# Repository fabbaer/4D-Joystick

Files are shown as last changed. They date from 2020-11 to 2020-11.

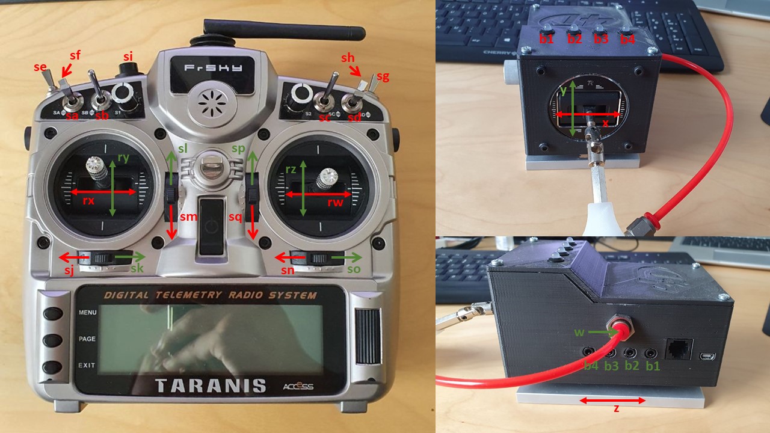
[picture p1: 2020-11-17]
documentation/mapping.jpg

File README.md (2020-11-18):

# 4D-Joystick

## Introduction
The 4D-Joystick allows people with physical disabilities to control complex RC-toys, like plains or multicopper. The RC-toys are controlled via a mouthpiece, a pressure sensor and movements of the head.

The system is divided into two units. The joystickunit is the user interface. It records the user inputs, processes them and forwards them to the remoteunit. The remoteunit is responsible for the communication with the RC-toy.

### Joystickunit
The joystickunit is the main part of the system and handles all user interactions. The heart of the system is a self-developed hardware with a Cortex-M4-Controller. The firmware offers a command-line-interface (CLI) via a USB connection to configure the system. Up to 32 different configurations can be stored on the joystickunit, each offering a flexible mapping of all inputs and outputs and configurations like deadzones. 

The joystickunit can either be powered via USB or via the remoteunit. All peripherals are placed inside a 3D-printed enclosure, which can be mounted on a stand. On the outside of the housing a display and a rotary button is placed, which can be used to load different configurations and display system information. Additionally, there are four headphone jacks to connect external buttons, which can be used to control the digital channels of the remote control. The buttons can be chosen to fit the user's needs and can for example be pressed with a foot or finger. 

The analogue channels are controlled via a mouthpiece. Three of the four degrees of freedom are controlled via movements of the head in up, down, left, right, forward and backward direction. The fourth degree of freedom is controlled via a pressure sensor, which is connected to the mouthpiece. 

The firmware of the joystickunit is designed to be future-proof. In future applications, the joystickunit can for example be used as an input device for a computer or a game console. However, none of these applications are currently implemented, but many parts of the firmware are designed that this can be easily done in future. 

### Remoteunit
The remoteunit handles the communication with the RC-toy. A conventional RC-toy-remote (FrSky Taranis X9D Plus v2019) with OpenTX as main firmware is used as a basis for this unit.

The joystickunit needs to gain control over the input-devices of the remote-control (joysticks and buttons). Therefore, an additional PCB is added to the remote, which is placed right between the input devices and the main controller board. It is able to read the input-devices and control the corresponding inputs of the main controller board. Additionally, it is able to communicate with the joystickunit via SPI.

If the joystick unit is connected to this hardware, the board samples the input devices and sends this data to the joystick unit, where it can be used as input data. Parallel to this, the joystick unit sends the data for the output channels, which are then set by the board accordingly. Therefore, the joystick unit gains full access over the inputs of the remote unit.

If the joystick unit is not connected to the remoteunit, the additional board acts transparent and copies the inputs directly to the outputs. Therefore, the remote control can be normally used without the joystick unit.

## Content
### Folder "firmware"
Contains the firmware of the joystickunit and the remoteunit. Both firmwares were originally developed in STM32CubeIDE. The corresponding project files for this IDE were also included in this directory. 

To flash the firmware to the units a JTAG-programmer (e.g. ST-Link) and an adapter (e.g. Olimex ARM-JTAG-20-10) is needed.
 
### Folder "hardware"
Contains the hardware for both units. The PCBs were developed in Autodesk EAGLE. However, the folder contains also a PDF of the schematics and GERBER-data for manufacturing.

**NOTE:** The bill of material can be found in the documentation-folder.

### Folder "mechanics"

Contains the 3D-models of the enclosure for the joystickunit, which can be printed with a 3D-printer. They were developed in Autodesk Fusion 360.

### Folder "documentation"
Contains a bill of material and some additional documentation for the system.

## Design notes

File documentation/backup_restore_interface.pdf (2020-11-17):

# 4D-Joystick – Backup and Restore Interface

## 1. Introduction

The CLI interface of the 4D-Joystick support an option to backup the configuration of the system and restore it later or on another device. The interface is described in this document.

Following synonyms are used in this document:

- Carriage Return → CR or \r (ASCII 0x0D)
- Line Feed → LF or \n (ASCII 0x0A)
- Acknowledge → ACK (ASCII 0x06)
- Negative Acknowledge → NAK (ASCII 0x15)
- Command Line Interface → CLI

Basically, the backup is a dump of the EEPROM, where all configurations are stored. The EEPROM data have a total size of 8448 bytes. The backup data is divided into 132 packages of 64 bytes, each separated by a carriage return.

## 2. Backup

The backup can be started by typing “backup” to the CLI (“backup\r”).
The CLI answers this with the four characters for a new line (CR, LF and two spaces). These characters can be ignored. Afterwards, the CLI starts sending the EEPROM contents in packages of 64 Byte (separated by CR).

After all packages are transmitted (132 packages total) a acknowledge (ACK) is sent.

Example (green = user input, yellow = CLI outputs, white = backup output):

## 3. Restore

The restore process can be started by typing “restore” to the CLI (“restore\r”). The CLI answers this with the four characters for a new line (CR, LF and two spaces). These characters can be ignored.

The CLI sends an ACK next, which shows, that the joystick is waiting for the backup data. The backup data must be transmitted in packages of 64 byte, each separated by a CR. Each package is answered with an ACK or a NACK. Before the next package can be transmitted, the ACK must be received (the joystick needs some time for processing each package).

After finishing the restore process the joystick will be restarted to load the new configuration.

If problems occur the joystick will answer with a NACK and immediately stop the restore-process. No data will be written to the EEPROM in this case.

Example (green = user input, yellow = CLI outputs, white = restore output):

> backup\r\r\n__
<package 1: 64 Byte of data>\r <package 2: 64 Byte of data>\r
<package 3: 64 Byte of data>\r
<package 132: 64 Byte of data>\r ACK \r\n >

> restore\r\r\n__
<package 1: 64 Byte of data>\r ACK <package 2: 64 Byte of data>\r ACK <package 3: 64 Byte of data>\r ACK
<package 132: 64 Byte of data>\r ACK \r\n >

## 4. Notes

The first few bytes of the EEPROM contain a special pattern, which is used to check if the storage is initialized. Each time the joystick boots up, this pattern is checked. If it is not valid, the joystick will override the storage with its default values.
However, in future firmware versions this pattern will be changed, if the storage structure will be changed. During the backup/restore process this pattern is copied/overwritten. Therefore, it will depend on the new firmware if restoring backups from old firmwares is accepted (migrating features must be implemented) or if they will be overwritten with default values, because the pattern is different.

The data from the EEPROM is sent as it is stored. In some terminal programs (for example “Putty”) this can lead to strange behaviour, because the raw data can accidently contain special characters or strings (chars used for control, escaped sequences, …). To correctly use the backup/restore function, the data must be processed raw and shall not be interpreted.

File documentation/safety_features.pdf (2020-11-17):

# 4D-Joystick – Safety features

## 1. Introduction

The 4D-Joystick has implemented some safety features, which provide safe operation. The main purpose is to avoid software and communication failures. This document gives an overview which and how safety features are implemented.

## 2. Communication

A SPI-interface is used to exchange data between the joystickunit (master) and the remoteunit (slave). The transfer speed is quite high, the cable is long and the remoteunit is a quite strong wireless transmitter which can also interfere with the SPI interface and the long cable. This all can lead to transfer failures.
Because a lot of packages get lost at high SPI frequencies (~20% of packages are lost at 2 MHz) the transfer frequency was reduced dramatically (40kHz). This led to a stable communication, where no packages get lost (at least as tested so far).

However, to further improve communication an additional safety step was implemented. Each package contains a CRC value, which can be checked at the receiver. If the CRC is wrong, the package is ignored and the last valid package is used for the next cycle. Because the communication cycle is quite short (~4ms) the user will not even notice if a single package gets lost.

If a lot of package get lost (25 consecutive packages) the remoteunit will switch to a failsafe mode. It will update the output with the inputs of the remote, like it does in teacher mode or without a joystickunit, at a reduced rate (once every 100ms). The remoteunit will try to start communication with the joystickunit again and switches to normal operation as soon as a valid package is received.

## 3. Remoteunit

The firmware of the remoteunit is a quite simple software, which is running in a loop. Every loop is one full communication cycle with the joystickunit (read inputs, send inputs to joystickunit, receive outputs from joystickunit, set outputs).
However, to avoid that the software is stuck somewhere in this loop a watchdog is used. The watchdog is a hardware peripheral of the controller which resets the device if it not reaches certain checkpoints in a fixed period.

In case of the remoteunit this checkpoint is set at the end of the loop, after the outputs are set. Normally this checkpoint should be reached every ~4ms. However, especially during first run this can take longer, because initialization is not finished and the first communication cycle can be missed. For this reason, the watchdog is configured to reset the controller when loop execution takes longer than 15ms.

## 4. Joystickunit

The joystickunit also uses a watchdog to ensure that software didn’t stuck somewhere, but the firmware is more complex because it used a RTOS. Therefore, the software does not run in one simple loop, but is divided in task which run in loops. There are five tasks:

- system-task: is called every ~250ms with middle priority and handles general system work (debug-led, voltage monitoring, …).
- remoteunit-task: is called every ~4ms with high priority and handles communication with joystickunit and processing of the related data
- buttons-task: is called every ~2ms with middle priority and handles all button inputs (buddybuttons and rotary encoder).
- userinterface-task: is called every ~100ms with low priority and handles the display and interpretation of the rotary encoder.
- CLI-task: is called every ~10ms with low priority and handles command line inputs.

For a save operation it is mandatory that the remoteunit-task, the system-task and the buttons-task is executed periodically. The other tasks are not mandatory for main operation (only for configuration).

However, only one task can be monitored by the watchdog. Due to design decisions the system-task is monitored. The watchdog of this controller is more advanced than the remoteunit-watchdog and has a window mode. For this reason, the watchdog not only checks if the checkpoint was reached within a fixed time, but also check if the time was to short to reach the checkpoint (f.e. because the checkpoint itself is stuck in a loop).

Normally the system task should be executed every ~250ms. The watchdog will reset the controller if time between execution of task is lower than ~150ms or if task is not executed for more than 300ms.

To monitor the other tasks a software-watchdog is implemented in the system-task. Each task must notify the system-task after each execution. The system-task counts the notifications for each task and knows a minimum value of execution during one system-task-cycle. If this minimum number is not reached, the system-task will reset the controller.

Minimum amount of execution during one system-task-cycle (~250ms):

- remoteunit-task: 30 (should normally be ~60)
- buttons-task: 60 (should normally be ~120)
- userinterface-task: 1 (should normally be 2 or 3)

However, the CLI-task is not monitored. It is blocked during command-execution and user inputs and therefore cycle time has high variances and is depended on the user.
It is not mandatory that CLI-task is working correctly for main operation. The user will notice if this task is stuck and can restart the joystick on his own.

Therefore, the system-task is monitored by the watchdog and every other task (expect CLI-task) is monitored by the system-task. This leads to a safe system (at least in relation to stuck of software).

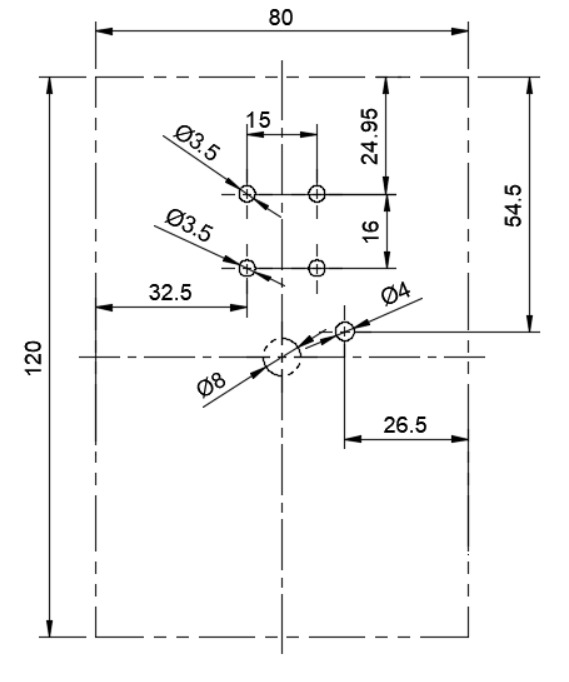
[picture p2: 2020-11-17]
mechanics/base_plate.jpg

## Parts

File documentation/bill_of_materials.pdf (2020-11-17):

Reference | Pcs. | Manufacturer | Partnumber | Description | Farnell Order# | RS Order# | Comment
PCB | 1 | | | PCB for Joystickunit
VD1, VD2 | 2 | Littlefuse | PGB102ST23WR | ESD Supressordiode | 1757241 | 760-6762
U1 | 1 | Microchip | MCP23018-E/S | GPIO Expander | 1854490 | 770-9729
U2 | 1 | STMicroelectronics | STM32F410RBT6 | Microcontroller | 2518136 | 914-8158
J1 | 1 | TE Connectivity | 5555165-1 | RJ25 Connector | 2778793 | 782-0826
J2 | 1 | Samtec | FTSH-105-01-F-DV-K | JTAG Header | 2856430 | 159-2372
IC1 | 1 | Texas Instruments | DAC124S085CIMM | DAC, 4 Channel | 3118597 | 651-2026
IC2 | 1 | ON Semiconductor | MC33269DR2-3.3G | LDO, 3V3 | 2534303 | 785-6894
C1 - C9 | 9 | | | Capacitor 0603, 100nF
C10 - C13 | 4 | | | Capacitor 0603, 1uF
C15, C16 | 2 | | | Capacitor 0603, 10uF
C20 | 1 | | | Capacitor 0603, 4.7uF
R1 - R8 | 8 | | | Resistor 0603, 10k
R10 | 1 | | | Resistor 0603, 150R
LED1 | 1 | | | LED 0603, grün
Cabling | 2 | JST | B12B-PH-K-S | JST PH Connector 12-way | 9492470 | 820-1425
| 2 | JST | PHR-12 | JST PH Connector 12-way | | 175-4836
| 1 | Molex | 15134-1403 | Picoblade Connector 14-way with cables 30cm | 2841009
| 2 | Molex | 53047-1411 | Picoblade Connector 14 way | 9732900
| 2 | JST | B5B-PH-K-S | JST PH Connector 5-way | | 820-1438
| 2 | JST | PHR-5 | JST PH Connector 5-way | | 820-1472
| 29 | JST | 01SPHSPH-26L-300 | Cable for JST-PH-series, 30cm | | 820-1412
Mounting | 2 | Richco | HTSN-M3-6-6-1 | Spacers, 6mm, M3 | | 102-6356
| 2 | Wurth Elektronik | 963060042 | Spacers, 6mm | 2987770
| 2 | | | Screw, M3, 5mm | | | Amazon (https://www.amazon.de/gp/product/B07Q8SKW9B/ref=ppx_yo_dt_b_search_asin_title?ie=UTF8&psc=1)
| 2 | | | Tapping screw, M2.5, 16mm, | | | Amazon (https://www.amazon.de/gp/product/B01LQGAX3U/ref=ppx_yo_dt_b_search_asin_title?ie=UTF8&psc=1)

## 4D-Joystick - BOM - Remoteunit

Reference | Pcs. | Manufacturer | Partnumber | Description | Farnell Order# | RS Order# | Comment
PCB | 1 | | | PCB for Joystickunit
VD1 - VD6 | 6 | Littlefuse | PGB102ST23WR | ESD Supressordiode | 1757241 | 760-6762
U1 | 1 | STMicroelectronics | STM32L476RET6 | Microcontroller | 2494459
IC1 | 1 | Microchip | 24AA256-I/SN | EEPROM 256 Kbit | 1331295 | 667-8246
IC2 | 1 | NXP | MPXV7007DP | Pressuresensor | 2776036
IC3 | 1 | Texas Instruments | TPS211APW | PowerMux | 3009619 | 665-8866
IC4 | 1 | ON Semiconductor | MC33269DR2-3.3G | LDO, 3V3 | 2534303 | 785-6894
J1 | 1 | TE Connectivity | 5555165-1 | RJ25 Connector | 2778793 | 782-0826
J2 | 1 | Samtec | FTSH-105-01-F-DV-K | JTAG Header | 2856430 | 159-2372
J3, J4, J5, J6 | 4 | Cliff Electronic | FC68125 | Phone Jack, 3.5mm | 2309468 | 805-1655
J7 | 1 | Molex | 56579-0519 | USB Connector | 1125347 | 515-2011
J8 | 1 | JST | B12B-PH-K-S | Joystick Connector | 9492470 | 820-1425
P1, P4 | 2 | Molex | 53047-0610 | Picoblade Connector 6 way | 9733078 | 279-9235
P2 | 1 | Molex | 53047-1210 | Picoblade Connector 12 way | 9732896 | 319-1070
P3 | 1 | Molex | 53047-0310 | Picoblade Connector 3 way | 9732853 | 319-1064
LED1 | 1 | | | LED 0603, grün
C1 - C9 | 9 | | | Capacitor 0603, 100nF
C15 - C18 | 4 | | | Capacitor 0603, 1uF
C20 - C24 | 5 | | | Capacitor 0603, 10uF
C30 | 1 | | | Capacitor 0603, 470pF
R1 - R5 | 5 | | | Resistor 0603, 150R
R6 - R9 | 4 | | | Resistor 0603, 180R
R10, R11 | 2 | | | Resistor 0603, 1k
R15 | 1 | | | Resistor 0603, 4k7
R20 - R25 | 6 | | | Resistor 0603, 100k
R30 - R40 | 11 | | | Resistor 0603, 10k

## 4D-Joystick - BOM - Joystickunit PCB

Reference | Pcs. | Manufacturer | Partnumber | Description | Farnell Order# | RS Order# | Comment
Peripherals | 1 | FrSky | M9-R | Taranis X9D Plus M9-R Gimbal | | | modell-hubschrauber (https://www.modell-hubschrauber.at/Sender-Empfaenger-Module-und-Zubehoer/Sender-Ersatzteile/FrSky-Taranis-Sender-Ersatzteile/FrSKY-Taranis-X9D-Plus-M9-R-Gimba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)
| 1 | Alps | 402125 | Alps Fader 10k 60mm | | | www.conrad.at (https://www.conrad.at/de/p/alps-402125-mischpult-fader-10-k-mono-0-2-w-linear-1-st-441817.html)
| 1 | Bourns | PEC11R-4115F-S0018 | Rotary Encoder | | 737-7736
| 1 | Mentor | 505.61 | Knob for rotary encoder | | | www.conrad.at (https://www.conrad.at/de/p/mentor-505-61-drehknopf-aluminium-x-h-12-mm-x-12-mm-1-st-183674.html)
| 1 | Heltec | 0.96 OLED | OLED Display, SPI, double colored | | | www.heltec.org (https://heltec.org/project/096-oled/)
| 4 | Broadcom Limited | HLMP-4000 | LED 5mm, Red/Green | 1003244
| 4 | VCC | CLP127BLK | LED Clip | 2293486
| 4 | VCC | RNG 268 | LED Sicherungsring | 2293489
Cabling | 1 | Molex | 15134-0603 | Picoblade Connector 6-way with cables 30cm | 2671469
| 1 | Molex | 15134-0303 | Picoblade Connector 3-way with cables 30cm | 2913933
| 1 | Molex | 15134-1203 | Picoblade Connector 12-way with cables 30cm | 2841003
Pneumatic | 1 | Norgren | PA0104025 | Tube 2.5mm | | | www.conrad.at (https://www.conrad.at/de/p/norgren-druckluftschlauch-pa0104025-polyamid-rot-innen-durchmesser-2-5-mm-28-bar-meterware-581694.html)
| 1 | Norgren | C00290400 | Tube Connector, 4mm | | | www.conrad.at (https://www.conrad.at/de/p/norgren-gerade-verbinder-c00290400-rohr-4-mm-1-st-582063.html)
| 1 | Norgren | C02250405 | Tube Connector, 4mm | | | www.conrad.at (https://www.conrad.at/de/p/norgren-gerade-verbinder-c02250405-aussengewinde-m5-rohr-4-mm-1-st-582818.html)
Mechanic | 1 | | | Aluminum Profil, 120x80x8mm | | | www.prokilo.at
| 1 | Hiwin | MGN09H | Carriage for guide rail
| 1 | Hiwin | MGN09R | Guide rail, 120mm
| 2 | Duratool | D01488 | Spacer, M3, 8mm | 1733419
| 1 | | | Cardan joint | | | www.conrad.at (http://www.conrad.at/ce/de/product/382136/Robbe-Navy-Kardan-35-1-1596/SHOP_AREA_32432)
| 1 | | | 3D printed Mouthpice
| 1 | | | 3D printed Housing
| 1 | | | 3D printed Housing-Lid
Mounting | 4 | Toolcraft | 889761 | Contersunk screw, M3, 10mm | | | www.conrad.at (https://www.conrad.at/de/p/toolcraft-889761-senkschrauben-m3-10-mm-kreuzschlitz-phillips-din-965-stahl-verzinkt-1-st-889761.html)
| 2 | Toolcraft | 888673 | Screw, M2.5, 5mm | | | www.conrad.at (https://www.conrad.at/de/p/toolcraft-889761-senkschrauben-m3-10-mm-kreuzschlitz-phillips-din-965-stahl-verzinkt-1-st-889761.html)
| 4 | Toolcraft | 888738 | Cylinder bolt, M3, 10mm | | | www.conrad.at (https://www.conrad.at/de/p/toolcraft-888738-zylinderschrauben-m3-10-mm-innensechskant-din-912-edelstahl-a2-1-st-888738.html)
| 4 | Toolcraft | 888718 | Hex nut, M3 | | | www.conrad.at (https://www.conrad.at/de/p/toolcraft-888718-sechskantmuttern-m3-din-934-stahl-verzinkt-1-st-888718.html)
| 6 | Toolcraft | TO-5430903 | Screw, M3, 10mm | | | www.conrad.at (https://www.conrad.at/de/p/toolcraft-to-5430903-linsenzylinderschrauben-m3-10-mm-kreuzschlitz-phillips-iso-7046-stahl-galvanisch-verzinkt-200-st-1810301.html)
| 4 | | | Screw, M3, 5mm | | | Amazon (https://www.amazon.de/gp/product/B07Q8SKW9B/ref=ppx_yo_dt_b_search_asin_title?ie=UTF8&psc=1)
| 8 | RS PRO | 278-534 | Threaded insert, M3 | | 278-534
| 4 | Toolcraft | 888674 | Screw, M2, 10mm | | | www.conrad.at (https://www.conrad.at/de/p/toolcraft-888674-zylinderschrauben-m2-10-mm-schlitz-din-84-stahl-verzinkt-1-st-888674.html)
| 4 | Toolcraft | 216364 | Hex nut, M2 | | | www.conrad.at (https://www.conrad.at/de/p/toolcraft-216364-sechskantmuttern-m2-din-934-messing-20-st-216364.html)

## 4D-Joystick - BOM - Joystickunit Peripherals, Cabling and Mechanics

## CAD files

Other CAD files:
mechanics/enclosure_bottom.f3d
mechanics/enclosure_top.f3d

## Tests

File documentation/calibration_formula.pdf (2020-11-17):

# 4D-Joystick – Calibration calculation

## 1. Introduction

The calibration-data are global attributes of the system and not related to different model-configurations. For every input channel (x, y, z and w on 4D-Joystick) and every output channel (x, y, z, and w on remote-unit) the three following values are stored:

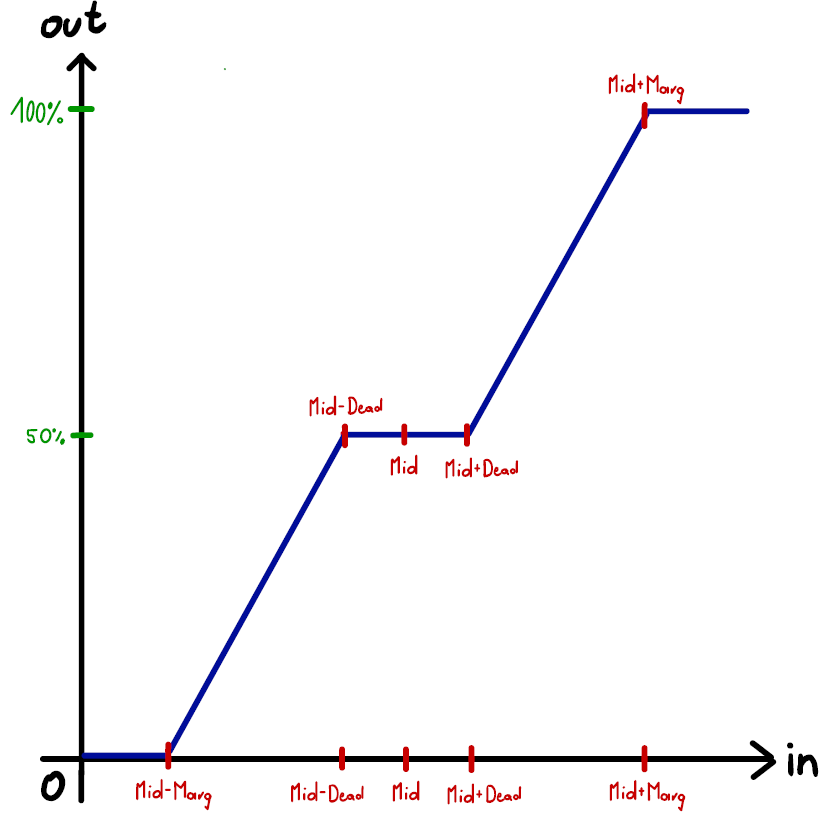
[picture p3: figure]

- Midpoint
The analogue value when the joysticks is in middle
position.
- Margin
The maximum movement from midpoint to one of the endpoints. Therefore, every channel theoretically has two margins (an upper and a lower one). However, only the bigger of both ones is stored. Value can be from 1 to 2047 and is automatically determined during calibration.
- Inversion
Stores if the channel is inverted.

Additionally, every input channel can have a deadzone. Unlike the other calibration-data, the deadzone is related to the model-configuration and not to the systemwide configuration.
The deadzone is an area around the midpoint of an analogue input, where output value keeps constant at the midpoint-value. It can be a value between 0 and 255.

## 2. Calculation

To reduce calculation-time for the analogue channels and their calibration-data, a simple formula with constant parameters is calculated. The calculation is done in three steps.
First of all, the input channel is normalized. This means that the values are modified in a way to use the full scale (12bit, 0-4095) for the maximum movement of the joystick (from bottom/left to top/right).
Then the same is done for output channel, but in the other direction. The full-scale input-value is modified in a way, that it depicts the maximum movement of the output joystick.
Finally the two calculation are combined to get a single formula. At runtime, the parameters for this formula are calculated when a configuration is loaded and can then be used for calculation of the analogue channels at every communication-cycle. This method is more efficient then calculating every step in every communication-cycle.

The formula for the output channel is a simple linear equation. However, the calculation for the input channel is more complex. This is mainly caused by the additional deadzone-parameter. For this reason, the calculation is separated into three linear equations which are related to different areas of the input-values.

### 2.1 Parameters

midI … Midpoint of input cℎannel margI … Margin of input cℎannel deadI … Deadzone of input cℎannel xI …Analogue input value
yI … Normalized value from input midO … Midpoint of output cℎannel
margO … Margin of output cℎannel
xO …Normalized value for output calculation yO … Analogue output value
FS …Full scale value (2

12 = 4096)

### 2.2 Input Channel

As mentioned before, the calculation is separated into three different areas.

Lower area | Deadzone | Upper area
xI < (midI − deadI ) | (midI − deadI ) ≥ xI and (midI + deadI ) ≤ xI | xI > (midI + deadI )
yI = kI ∗ xI + dI,L FS kI = 2 (margI − deadI ) dI,L = −kI ∗ (midI − margI ) | FS yI = 2 | yI = kI ∗ xI + dI,H FS kI = 2 (margI − deadI ) FS dI,H = −kI ∗ (midI + deadI ) + 2

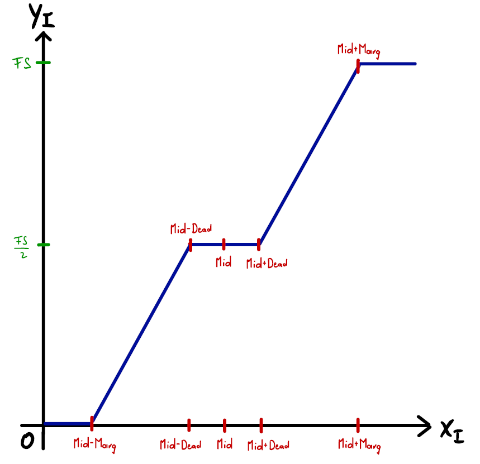
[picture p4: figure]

### 2.3 Output Channel

The calculation for the output channel is a linear equation:

yO = kO ∗ xO + dO

kO =

2 ∗ margO
FS
dO = midO − margO

### 2.4 Combination of input and output channel

Finally, both calculations are combined:

xO = yI

yO = kO ∗ yI + dO

yO = kO ∗ (kI ∗ xI + dI,(L/H)

) + dO

yO = kO ∗ kI ∗ xI + kO ∗ dI,(L/H) + dO

yO = k ∗ xI + d(L/H)

k = kO ∗ kI =

2 ∗ margO
FS

∗

FS
2 (margI−deadI)

=

margO
margI−deadI

d(L/H) = kO ∗ dI,(L/H) + dO

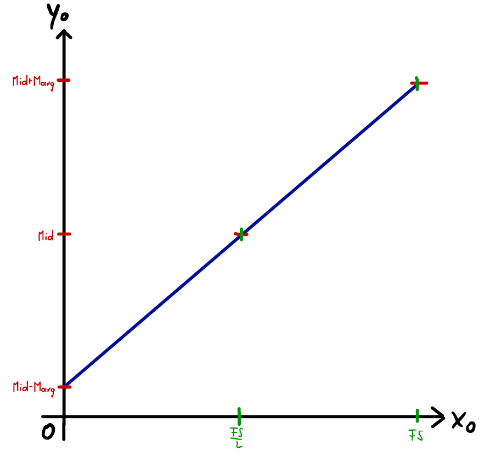
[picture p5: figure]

Lower area | Deadzone | Upper area
xI < (midI − deadI ) | (midI − deadI ) ≥ xI and (midI + deadI ) ≤ xI | xI > (midI + deadI )
dL = −kO ∗ kI ∗ (midI − margI ) + dO dL = −k ∗ (midI − margI ) + midO − margO margO k = margI − deadI yO = k ∗ xI + dL | FS yI = 2 yO = kO ∗ yI + dO yO = midO | FS dH = −kO ∗ kI ∗ (midI + deadI ) + kO + dO 2 dH = −k ∗ (midI + deadI ) + margO + midO − margO dH = −k ∗ (midI + deadI ) + midO margO k = margI − deadI yO = k ∗ xI + dH

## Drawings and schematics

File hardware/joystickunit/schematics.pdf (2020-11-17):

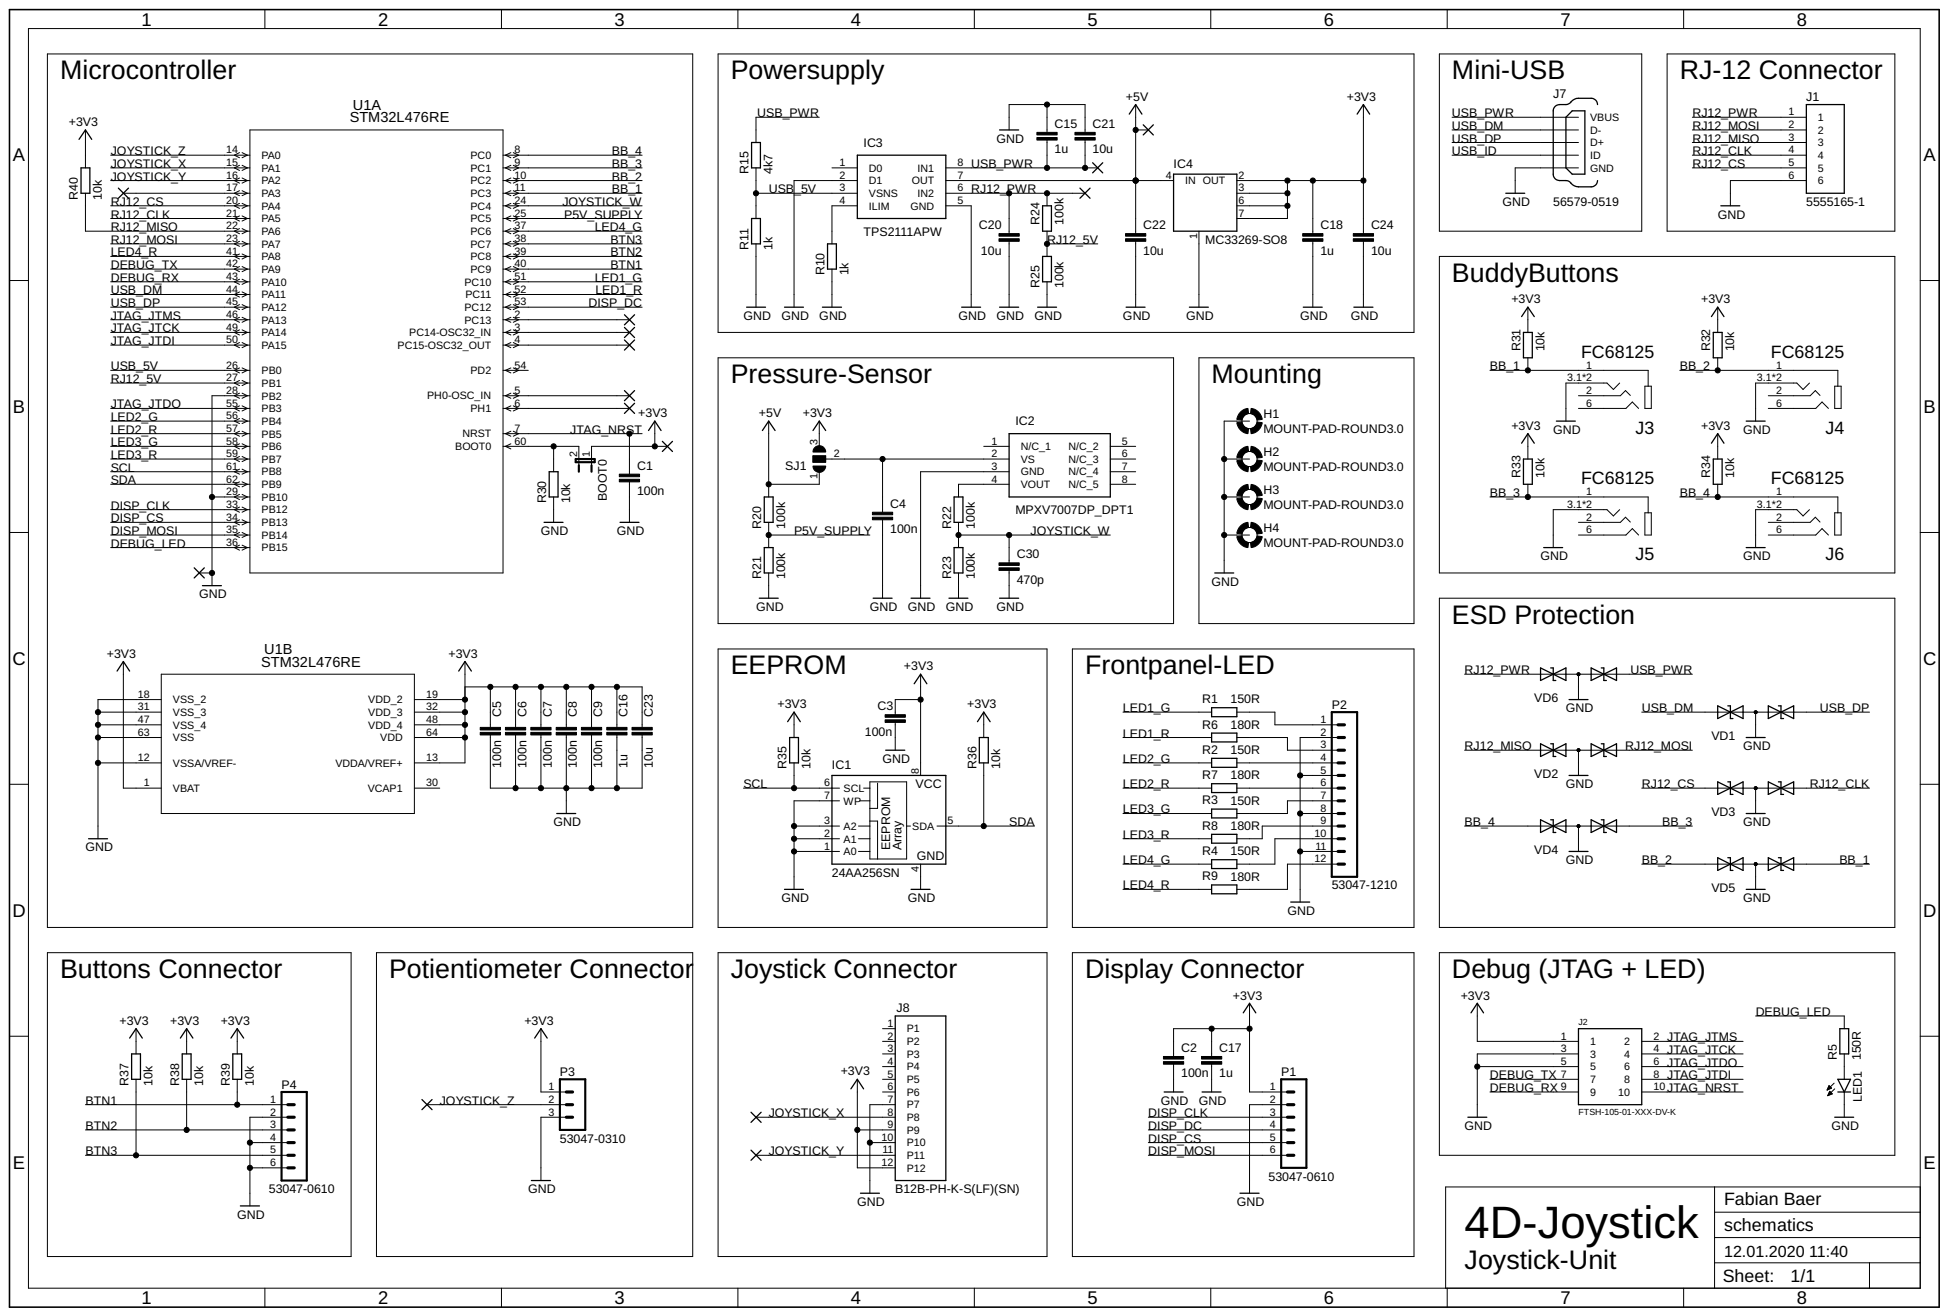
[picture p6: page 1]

MOUNT-PAD-ROUND3.0 MOUNT-PAD-ROUND3.0 MOUNT-PAD-ROUND3.0 MOUNT-PAD-ROUND3.0 GND

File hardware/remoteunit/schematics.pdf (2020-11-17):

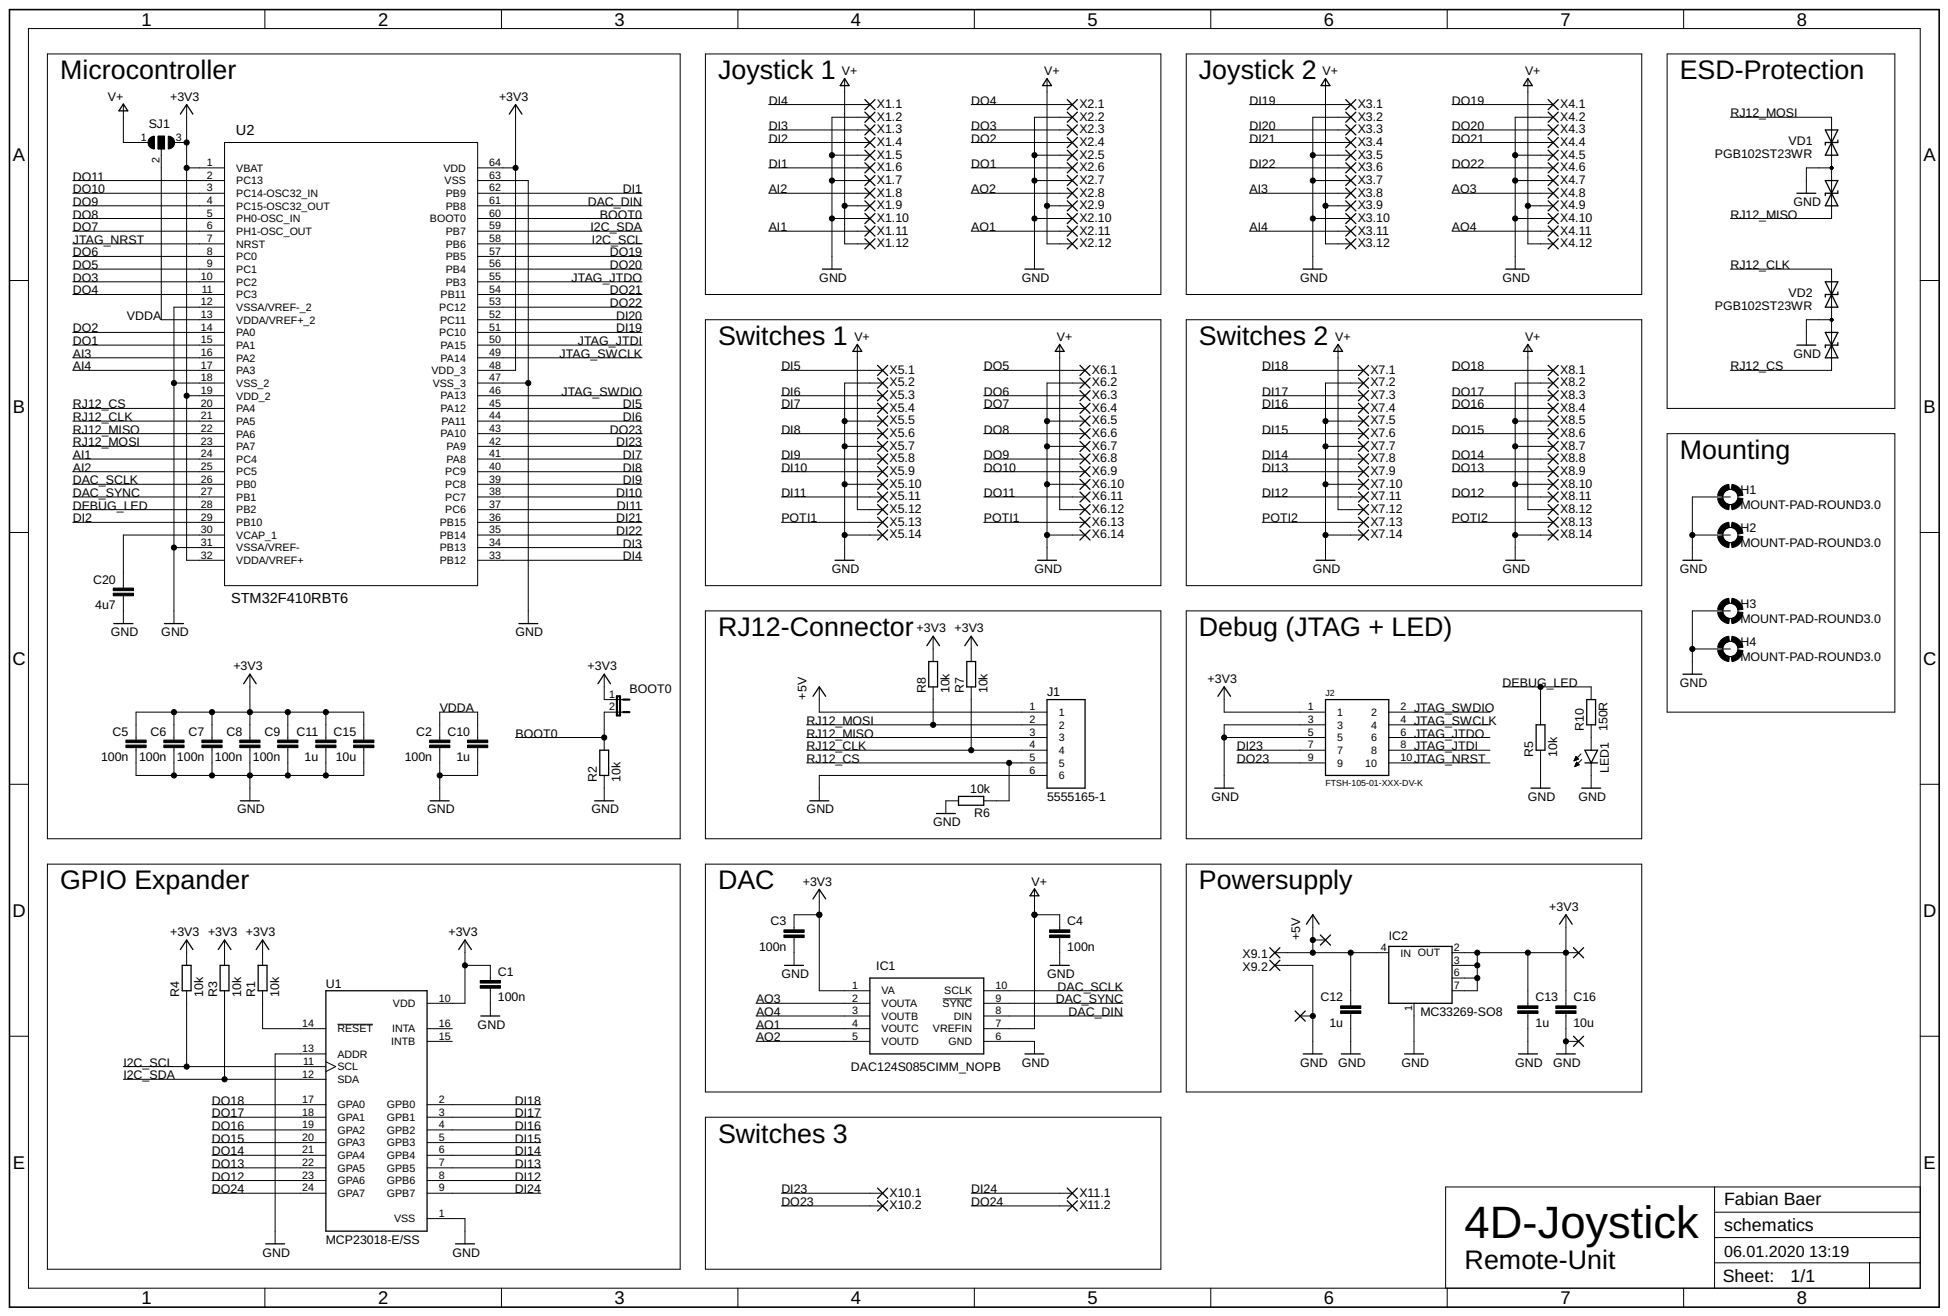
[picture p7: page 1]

MOUNT-PAD-ROUND3.0

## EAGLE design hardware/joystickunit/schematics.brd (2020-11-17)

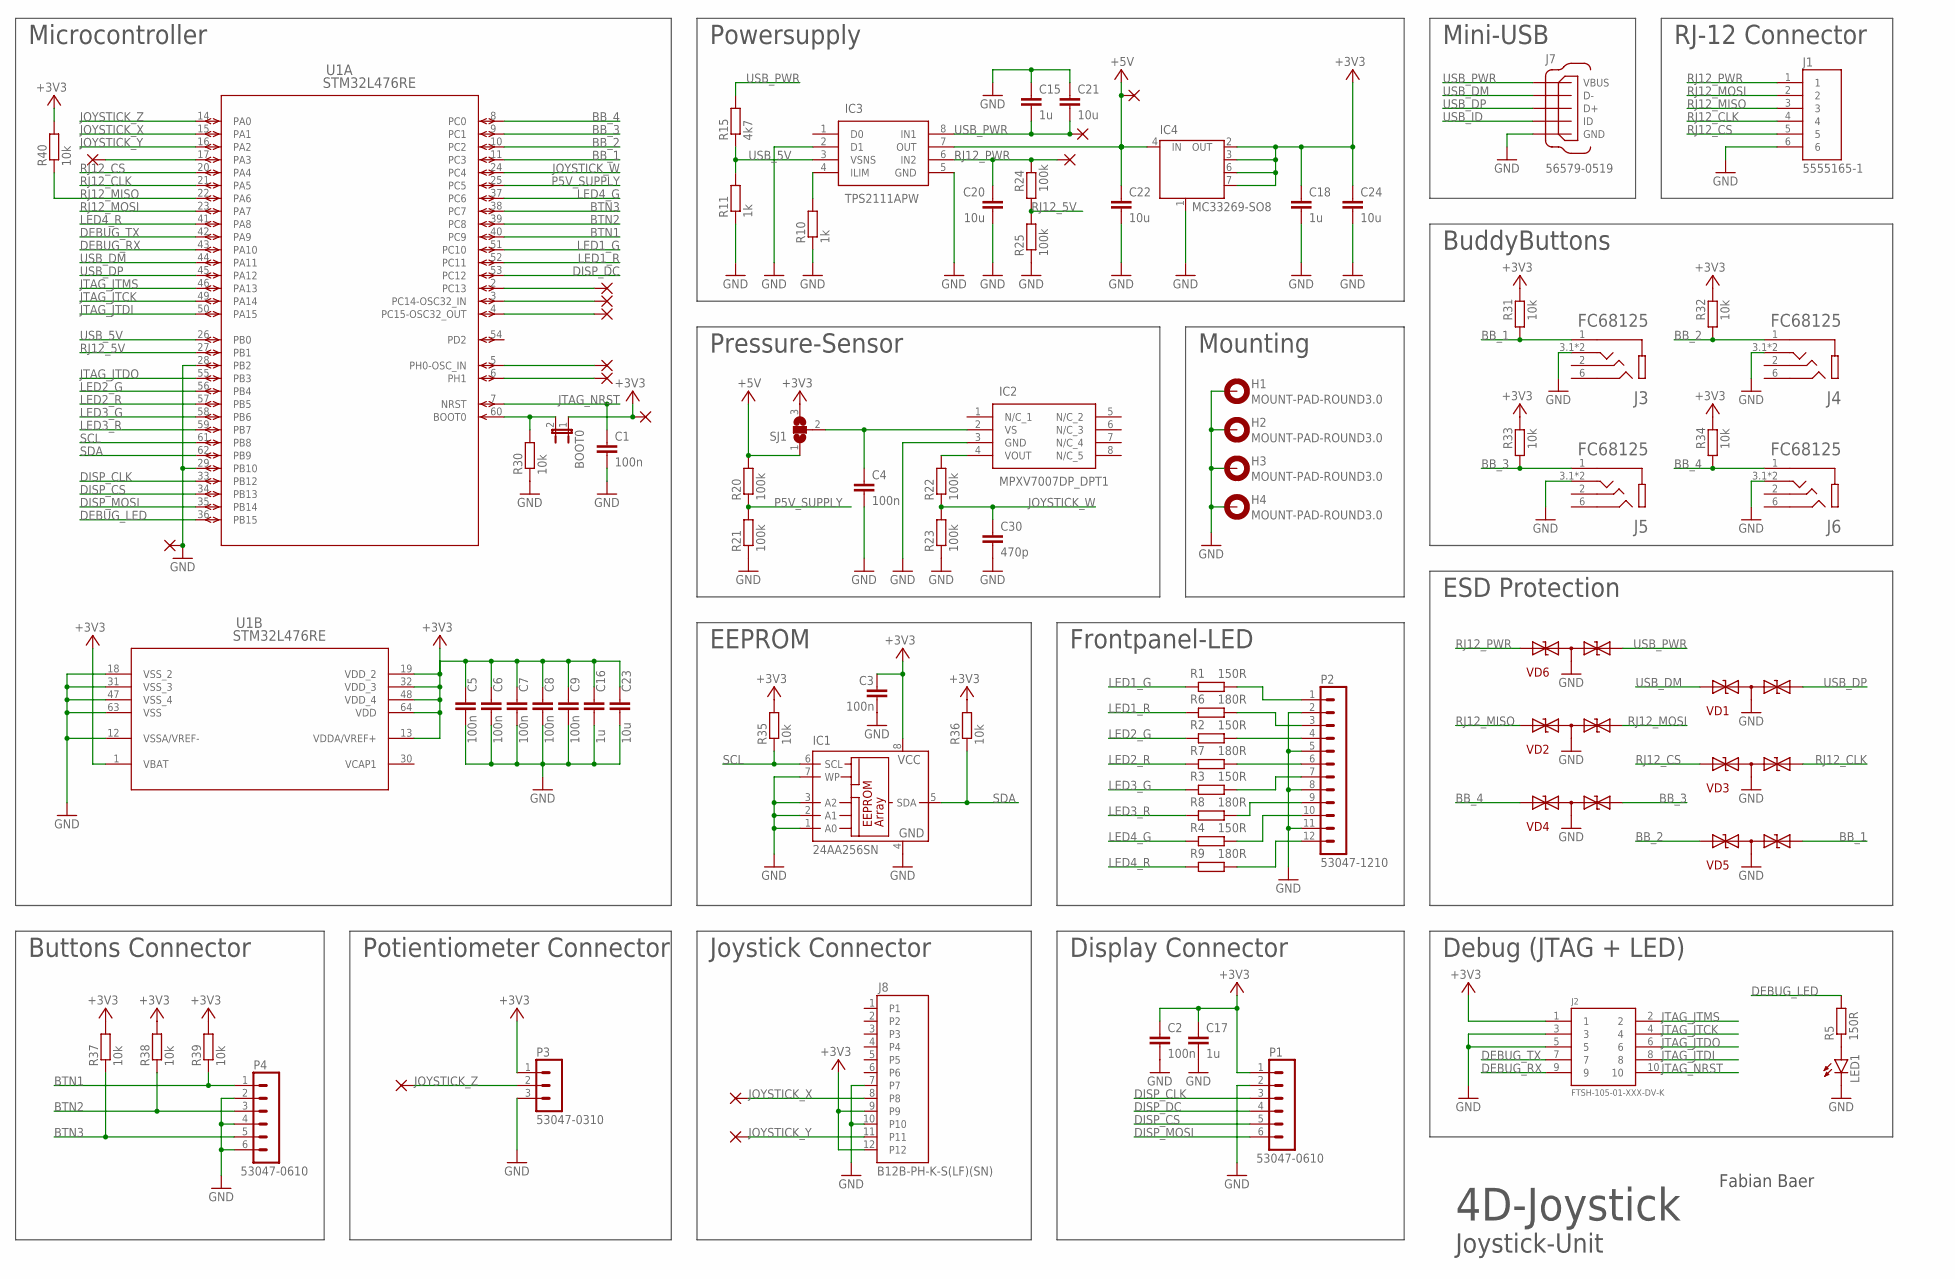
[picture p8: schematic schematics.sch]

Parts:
BOOT0: JP1E; JP1
C1, C2, C3, C4, C5, C6, C7, C8, C9: 100n; C0603
C15, C16, C17, C18: 1u; C0603
C20, C21, C22, C23, C24: 10u; C0603
C30: 470p; C0603
H1, H2, H3, H4: MOUNT-PAD-ROUND3.0; 3,0-PAD
IC1: 24AA256SN; SO-08
IC2: MPXV7007DP_DPT1; MPXV7007DPDPT1
IC3: TPS2111APW; SOP65P640X120-8N
IC4: MC33269-SO8; SO08
J1: 5555165-1; TE_5555165-1
J2: FTSH-105-01-XXX-DV-K
J3, J4, J5, J6: FC68125; CLIFF_FC68125
J7: 56579-0519; MOLEX_56579-0519
J8: B12B-PH-K-S(LF)(SN); JST_B12B-PH-K-S(LF)(SN)
LED1: LEDSML0603; SML0603
P1, P4: 53047-0610
P2: 53047-1210
P3: 53047-0310
PAD1, PAD2, PAD3, PAD4, PAD5, PAD6, PAD7, PAD8, PAD9, PAD10, PAD11, PAD12, PAD13, PAD14: WIREPAD1,6/0,9; 1,6/0,9
R1, R2, R3, R4, R5: 150R; R0603
R6, R7, R8, R9: 180R; R0603
R10, R11: 1k; R0603
R15: 4k7; R0603
R20, R21, R22, R23, R24, R25: 100k; R0603
R30, R31, R32, R33, R34, R35, R36, R37, R38, R39, R40: 10k; R0603
SJ1: SJ2W; SJ_2
U1: STM32L476RE; LQFP64-10X10MM
VD1, VD2, VD3, VD4, VD5, VD6: PGB102ST23WR; SOT23

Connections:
+3V3: BOOT0.1, C2.1, C3.1, C5.1, C6.1, C7.1, C8.1, C9.1, C16.1, C17.1, C18.1, C23.1, C24.1, IC1.8 (VCC), IC4.2 (OUT), IC4.3 (OUT), IC4.6 (OUT), IC4.7 (OUT), J2.1, J8.9, J8.12, P1.1, P3.1, PAD7.1, R31.2, R32.2, R33.2, R34.2, R35.2, R36.2, R37.2, R38.2, R39.2, R40.2, SJ1.3, U1.1 (VBAT), U1.13 (VDDA/VREF+), U1.19 (VDD_2), U1.32 (VDD_3), U1.48 (VDD_4), U1.64 (VDD)
+5V: C22.1, IC3.7 (OUT), IC4.4 (IN), PAD9.1, R20.2, SJ1.1
BB_1: J3.1 (1S), R31.1, U1.11 (PC3), VD5.1 (A)
BB_2: J4.1 (1S), R32.1, U1.10 (PC2), VD5.2 (A1)
BB_3: J5.1 (1S), R33.1, U1.9 (PC1), VD4.1 (A)
BB_4: J6.1 (1S), R34.1, U1.8 (PC0), VD4.2 (A1)
BTN1: P4.1, R39.1, U1.40 (PC9)
BTN2: P4.3, R38.1, U1.39 (PC8)
BTN3: P4.5, R37.1, U1.38 (PC7)
DEBUG_LED: R5.2, U1.36 (PB15)
DEBUG_RX: J2.9, U1.43 (PA10)
DEBUG_TX: J2.7, U1.42 (PA9)
DISP_CLK: P1.3, U1.33 (PB12)
DISP_CS: P1.5, U1.34 (PB13)
DISP_DC: P1.4, U1.53 (PC12)
DISP_MOSI: P1.6, U1.35 (PB14)
GND: C1.2, C2.2, C3.2, C4.2, C5.2, C6.2, C7.2, C8.2, C9.2, C15.1, C16.2, C17.2, C18.2, C20.2, C21.1, C22.2, C23.2, C24.2, C30.2, H1.B3,0, H2.B3,0, H3.B3,0, H4.B3,0, IC1.1 (A0), IC1.2 (A1), IC1.3 (A2), IC1.4 (GND), IC1.7 (WP), IC2.3 (GND), IC3.2 (D1), IC3.5 (GND), IC4.1 (GND/ADJ), J1.6, J2.3, J2.5, J3.3.1 (3T), J3.3.2 (3T), J4.3.1 (3T), J4.3.2 (3T), J5.3.1 (3T), J5.3.2 (3T), J6.3.1 (3T), J6.3.2 (3T), J7.5 (GND), J8.7, J8.10, LED1.C, P1.2, P2.2, P2.5, P2.8, P2.11, P3.3, P4.2, P4.4, P4.6, PAD8.1, R10.1, R11.1, R21.1, R23.1, R25.1, R30.1, U1.12 (VSSA/VREF-), U1.18 (VSS_2), U1.28 (PB2), U1.29 (PB10), U1.31 (VSS_3), U1.47 (VSS_4), U1.63 (VSS), VD1.3 (C), VD2.3 (C), VD3.3 (C), VD4.3 (C), VD5.3 (C), VD6.3 (C)
JOYSTICK_W: C30.1, R22.1, R23.2, U1.24 (PC4)
JOYSTICK_X: J8.8, PAD12.1, U1.15 (PA1)
JOYSTICK_Y: J8.11, PAD13.1, U1.16 (PA2)
JOYSTICK_Z: P3.2, PAD14.1, U1.14 (PA0)
JTAG_JTCK: J2.4, U1.49 (PA14)
JTAG_JTDI: J2.8, U1.50 (PA15)
JTAG_JTDO: J2.6, U1.55 (PB3)
JTAG_JTMS: J2.2, U1.46 (PA13)
JTAG_NRST: C1.1, J2.10, U1.7 (NRST)
LED1_G: R1.2, U1.51 (PC10)
LED1_R: R6.2, U1.52 (PC11)
LED2_G: R2.2, U1.56 (PB4)
LED2_R: R7.2, U1.57 (PB5)
LED3_G: R3.2, U1.58 (PB6)
LED3_R: R8.2, U1.59 (PB7)
LED4_G: R4.2, U1.37 (PC6)
LED4_R: R9.2, U1.41 (PA8)
unnamed: BOOT0.2, R30.2, U1.60 (BOOT0)
unnamed: C4.1, IC2.2 (VS), SJ1.2
unnamed: IC2.4 (VOUT), R22.2
unnamed: LED1.A, R5.1
unnamed: PAD1.1, U1.6 (PH1)
unnamed: PAD2.1, U1.5 (PH0-OSC_IN)
unnamed: PAD3.1, U1.2 (PC13)
unnamed: PAD4.1, U1.3 (PC14-OSC32_IN)
unnamed: IC3.4 (ILIM), R10.2
unnamed: P2.12, R9.1
unnamed: PAD5.1, U1.4 (PC15-OSC32_OUT)
unnamed: P2.10, R4.1
unnamed: P2.9, R8.1
unnamed: P2.7, R3.1
unnamed: P2.6, R7.1
unnamed: P2.4, R2.1
unnamed: P2.3, R6.1
unnamed: P2.1, R1.1
unnamed: PAD6.1, U1.17 (PA3)
P5V_SUPPLY: R20.1, R21.2, U1.25 (PC5)
RJ12_5V: R24.1, R25.2, U1.27 (PB1)
RJ12_CLK: J1.4, U1.21 (PA5), VD3.1 (A)
RJ12_CS: J1.5, U1.20 (PA4), VD3.2 (A1)
RJ12_MISO: J1.3, R40.1, U1.22 (PA6), VD2.2 (A1)
RJ12_MOSI: J1.2, U1.23 (PA7), VD2.1 (A)
RJ12_PWR: C20.1, IC3.6 (IN2), J1.1, PAD11.1, R24.2, VD6.2 (A1)
SCL: IC1.6 (SCL), R35.1, U1.61 (PB8)
SDA: IC1.5 (SDA), R36.1, U1.62 (PB9)
USB_5V: IC3.3 (VSNS), R11.2, R15.1, U1.26 (PB0)
USB_DM: J7.2 (D-), U1.44 (PA11), VD1.2 (A1)
USB_DP: J7.3 (D+), U1.45 (PA12), VD1.1 (A)
USB_ID: J7.4 (ID)
USB_PWR: C15.2, C21.2, IC3.8 (IN1), J7.1 (VBUS), PAD10.1, R15.2, VD6.1 (A)
VCAP1: U1.30 (VCAP1)

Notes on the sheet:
Mini-USB
Debug (JTAG + LED)
RJ-12 Connector
BuddyButtons
EEPROM
Pressure-Sensor
4D-Joystick
Joystick-Unit
Fabian Baer
Microcontroller
Potientiometer Connector
Joystick Connector
Frontpanel-LED
Powersupply
Display Connector
Buttons Connector
ESD Protection
Mounting

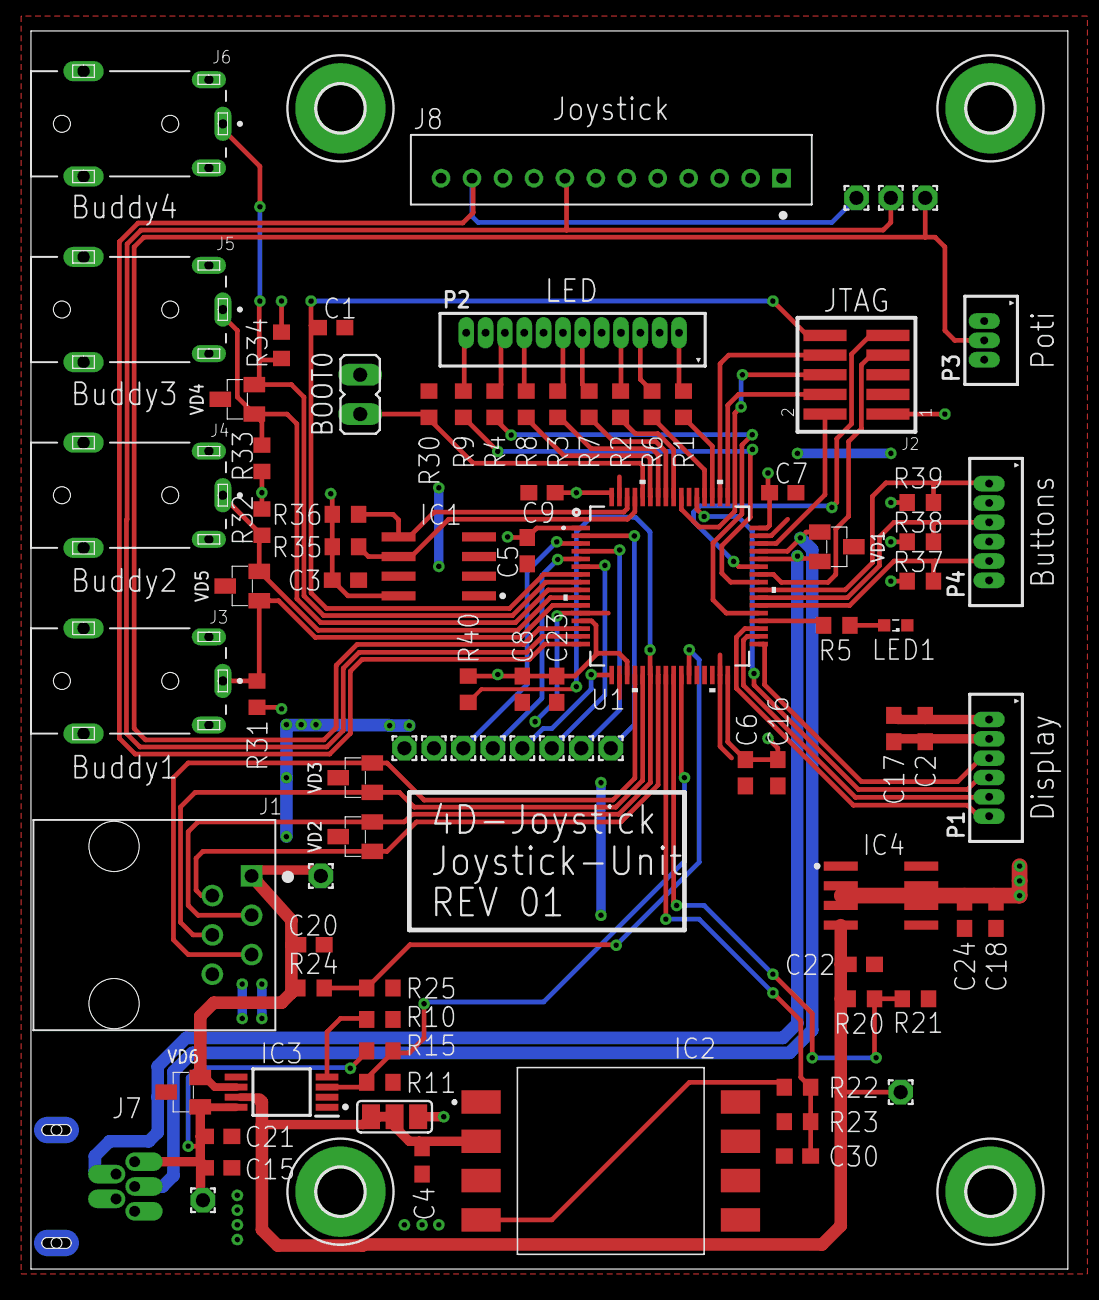
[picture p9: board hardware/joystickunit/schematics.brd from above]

Board: 2 copper layers, 67.0 x 80.0 mm, 92 parts (0 on the bottom side), 66 nets.

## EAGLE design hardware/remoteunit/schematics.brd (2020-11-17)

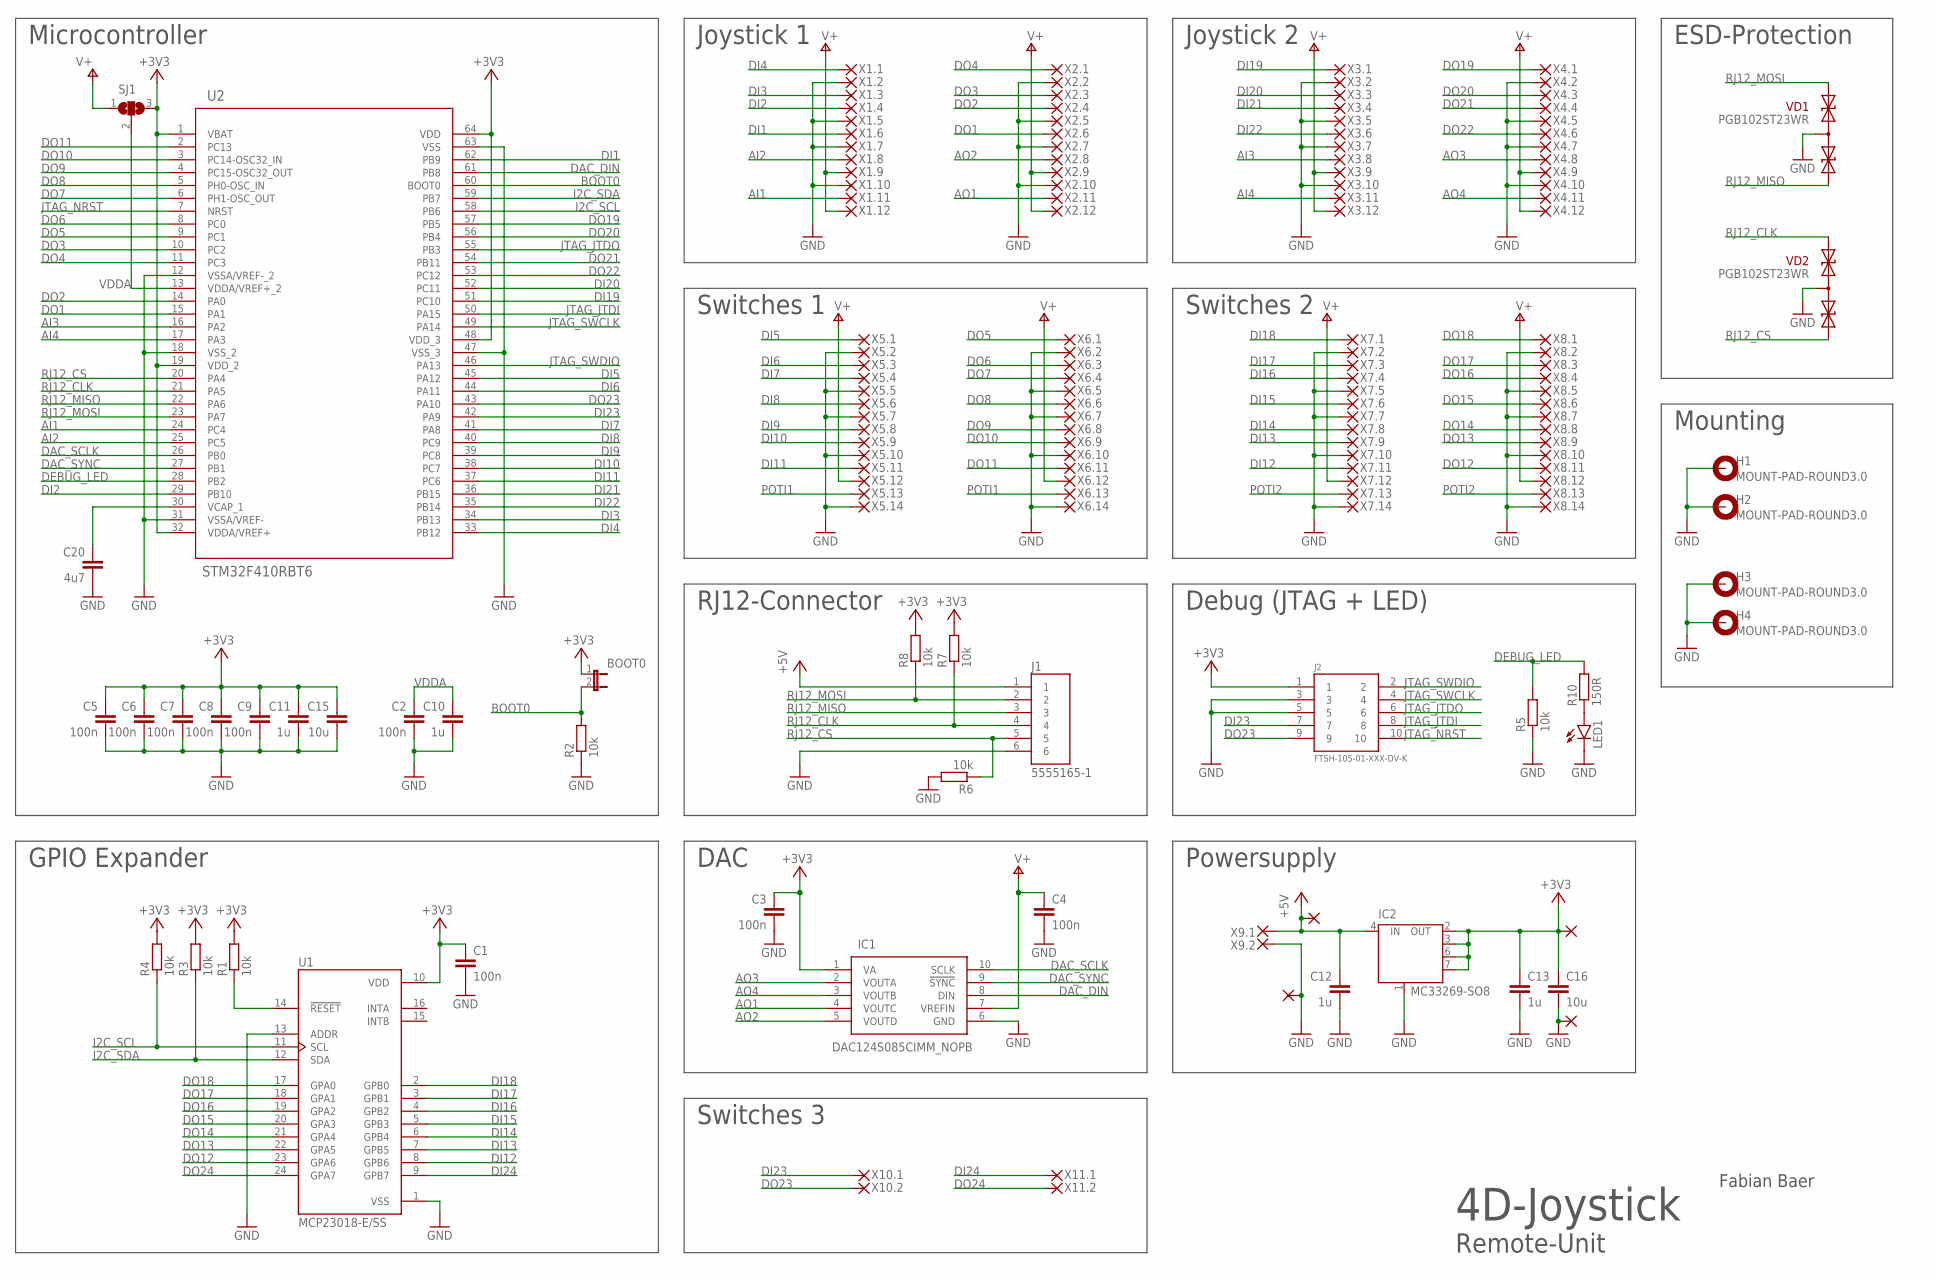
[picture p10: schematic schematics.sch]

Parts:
BOOT0: JP1E; JP1
C1, C2, C3, C4, C5, C6, C7, C8, C9: 100n; C0603
C10, C11, C12, C13: 1u; C0603
C15, C16: 10u; C0603
C20: 4u7; C0603
H1, H2, H3, H4: MOUNT-PAD-ROUND3.0; 3,0-PAD
IC1: DAC124S085CIMM_NOPB; SOP50P490X110-10N
IC2: MC33269-SO8; SO08
J1: 5555165-1; TE_5555165-1
J2: FTSH-105-01-XXX-DV-K
LED1: LEDSML0603; SML0603
R1, R2, R3, R4, R5, R6, R7, R8: 10k; R0603
R10: 150R; R0603
SJ1: SJ2W; SJ_2
U1: MCP23018-E/SS; SOP65P780X200-24N
U2: STM32F410RBT6; LQFP64-10X10MM
VD1, VD2: PGB102ST23WR; SOT23
X1.1, X1.2, X1.3, X1.4, X1.5, X1.6, X1.7, X1.8, X1.9, X1.10, X1.11, X1.12, X2.1, X2.2, X2.3, X2.4, X2.5, X2.6, X2.7, X2.8, X2.9, X2.10, X2.11, X2.12, X3.1, X3.2, X3.3, X3.4, X3.5, X3.6, X3.7, X3.8, X3.9, X3.10, X3.11, X3.12, X4.1, X4.2, X4.3, X4.4, X4.5, X4.6, X4.7, X4.8, X4.9, X4.10, X4.11, X4.12, X5.1, X5.2, X5.3, X5.4, X5.5, X5.6, X5.7, X5.8, X5.9, X5.10, X5.11, X5.12, X5.13, X5.14, X5.15, X5.16, X5.17, X5.18, X6.1, X6.2, X6.3, X6.4, X6.5, X6.6, X6.7, X6.8, X6.9, X6.10, X6.11, X6.12, X6.13, X6.14, X7.1, X7.2, X7.3, X7.4, X7.5, X7.6, X7.7, X7.8, X7.9, X7.10, X7.11, X7.12, X7.13, X7.14, X8.1, X8.2, X8.3, X8.4, X8.5, X8.6, X8.7, X8.8, X8.9, X8.10, X8.11, X8.12, X8.13, X8.14, X10.1, X10.2, X11.1, X11.2: WIREPAD1,6/0,9; 1,6/0,9
X9.1, X9.2: WIREPAD2,54/1,0; 2,54/1,0

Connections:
+3V3: BOOT0.1, C1.1, C3.1, C5.1, C6.1, C7.1, C8.1, C9.1, C11.1, C13.1, C15.1, C16.1, IC1.1 (VA), IC2.2 (OUT), IC2.3 (OUT), IC2.6 (OUT), IC2.7 (OUT), J2.1, R1.2, R3.2, R4.2, R7.2, R8.2, SJ1.3, U1.10 (VDD), U2.1 (VBAT), U2.19 (VDD_2), U2.32 (VDDA/VREF+), U2.48 (VDD_3), U2.64 (VDD), X5.15.1
+5V: C12.1, IC2.4 (IN), J1.1, X5.17.1, X9.1.1
AI1: U2.24 (PC4), X1.11.1
AI2: U2.25 (PC5), X1.8.1
AI3: U2.16 (PA2), X3.8.1
AI4: U2.17 (PA3), X3.11.1
AO1: IC1.4 (VOUTC), X2.11.1
AO2: IC1.5 (VOUTD), X2.8.1
AO3: IC1.2 (VOUTA), X4.8.1
AO4: IC1.3 (VOUTB), X4.11.1
BOOT0: BOOT0.2, R2.2, U2.60 (BOOT0)
DAC_DIN: IC1.8 (DIN), U2.61 (PB8)
DAC_SCLK: IC1.10 (SCLK), U2.26 (PB0)
DAC_SYNC: IC1.9 (!SYNC), U2.27 (PB1)
DEBUG_LED: R5.2, R10.2, U2.28 (PB2)
DI1: U2.62 (PB9), X1.6.1
DI2: U2.29 (PB10), X1.4.1
DI3: U2.34 (PB13), X1.3.1
DI4: U2.33 (PB12), X1.1.1
DI5: U2.45 (PA12), X5.1.1
DI6: U2.44 (PA11), X5.3.1
DI7: U2.41 (PA8), X5.4.1
DI8: U2.40 (PC9), X5.6.1
DI9: U2.39 (PC8), X5.8.1
DI10: U2.38 (PC7), X5.9.1
DI11: U2.37 (PC6), X5.11.1
DI12: U1.8 (GPB6), X7.11.1
DI13: U1.7 (GPB5), X7.9.1
DI14: U1.6 (GPB4), X7.8.1
DI15: U1.5 (GPB3), X7.6.1
DI16: U1.4 (GPB2), X7.4.1
DI17: U1.3 (GPB1), X7.3.1
DI18: U1.2 (GPB0), X7.1.1
DI19: U2.51 (PC10), X3.1.1
DI20: U2.52 (PC11), X3.3.1
DI21: U2.36 (PB15), X3.4.1
DI22: U2.35 (PB14), X3.6.1
DI23: J2.7, U2.42 (PA9), X10.1.1
DI24: U1.9 (GPB7), X11.1.1
DO1: U2.15 (PA1), X2.6.1
DO2: U2.14 (PA0), X2.4.1
DO3: U2.10 (PC2), X2.3.1
DO4: U2.11 (PC3), X2.1.1
DO5: U2.9 (PC1), X6.1.1
DO6: U2.8 (PC0), X6.3.1
DO7: U2.6 (PH1-OSC_OUT), X6.4.1
DO8: U2.5 (PH0-OSC_IN), X6.6.1
DO9: U2.4 (PC15-OSC32_OUT), X6.8.1
DO10: U2.3 (PC14-OSC32_IN), X6.9.1
DO11: U2.2 (PC13), X6.11.1
DO12: U1.23 (GPA6), X8.11.1
DO13: U1.22 (GPA5), X8.9.1
DO14: U1.21 (GPA4), X8.8.1
DO15: U1.20 (GPA3), X8.6.1
DO16: U1.19 (GPA2), X8.4.1
DO17: U1.18 (GPA1), X8.3.1
DO18: U1.17 (GPA0), X8.1.1
DO19: U2.57 (PB5), X4.1.1
DO20: U2.56 (PB4), X4.3.1
DO21: U2.54 (PB11), X4.4.1
DO22: U2.53 (PC12), X4.6.1
DO23: J2.9, U2.43 (PA10), X10.2.1
DO24: U1.24 (GPA7), X11.2.1
GND: C1.2, C2.2, C3.2, C4.2, C5.2, C6.2, C7.2, C8.2, C9.2, C10.2, C11.2, C12.2, C13.2, C15.2, C16.2, C20.2, H1.B3,0, H2.B3,0, H3.B3,0, H4.B3,0, IC1.6 (GND), IC2.1 (GND/ADJ), J1.6, J2.3, J2.5, LED1.C, R2.1, R5.1, R6.2, U1.1 (VSS), U1.13 (ADDR), U2.12 (VSSA/VREF-_2), U2.18 (VSS_2), U2.31 (VSSA/VREF-), U2.47 (VSS_3), U2.63 (VSS), VD1.3 (C), VD2.3 (C), X1.2.1, X1.5.1, X1.7.1, X1.10.1, X2.2.1, X2.5.1, X2.7.1, X2.10.1, X3.2.1, X3.5.1, X3.7.1, X3.10.1, X4.2.1, X4.5.1, X4.7.1, X4.10.1, X5.2.1, X5.5.1, X5.7.1, X5.10.1, X5.14.1, X5.16.1, X5.18.1, X6.2.1, X6.5.1, X6.7.1, X6.10.1, X6.14.1, X7.2.1, X7.5.1, X7.7.1, X7.10.1, X7.14.1, X8.2.1, X8.5.1, X8.7.1, X8.10.1, X8.14.1, X9.2.1
I2C_SCL: R4.1, U1.11 (SCL), U2.58 (PB6)
I2C_SDA: R3.1, U1.12 (SDA), U2.59 (PB7)
JTAG_JTDI: J2.8, U2.50 (PA15)
JTAG_JTDO: J2.6, U2.55 (PB3)
JTAG_NRST: J2.10, U2.7 (NRST)
JTAG_SWCLK: J2.4, U2.49 (PA14)
JTAG_SWDIO: J2.2, U2.46 (PA13)
unnamed: R1.1, U1.14 (!RESET)
unnamed: C20.1, U2.30 (VCAP_1)
unnamed: LED1.A, R10.1
POTI1: X5.13.1, X6.13.1
POTI2: X7.13.1, X8.13.1
RJ12_CLK: J1.4, R7.1, U2.21 (PA5), VD2.2 (A1)
RJ12_CS: J1.5, R6.1, U2.20 (PA4), VD2.1 (A)
RJ12_MISO: J1.3, U2.22 (PA6), VD1.1 (A)
RJ12_MOSI: J1.2, R8.1, U2.23 (PA7), VD1.2 (A1)
V+: C4.1, IC1.7 (VREFIN), SJ1.1, X1.9.1, X1.12.1, X2.9.1, X2.12.1, X3.9.1, X3.12.1, X4.9.1, X4.12.1, X5.12.1, X6.12.1, X7.12.1, X8.12.1
VDDA: C2.1, C10.1, SJ1.2, U2.13 (VDDA/VREF+_2)

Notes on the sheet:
Microcontroller
Debug (JTAG + LED)
4D-Joystick
Remote-Unit
Fabian Baer
ESD-Protection
Powersupply
DAC
Joystick 1
Joystick 2
GPIO Expander
Switches 1
Switches 2
Mounting
Switches 3
RJ12-Connector

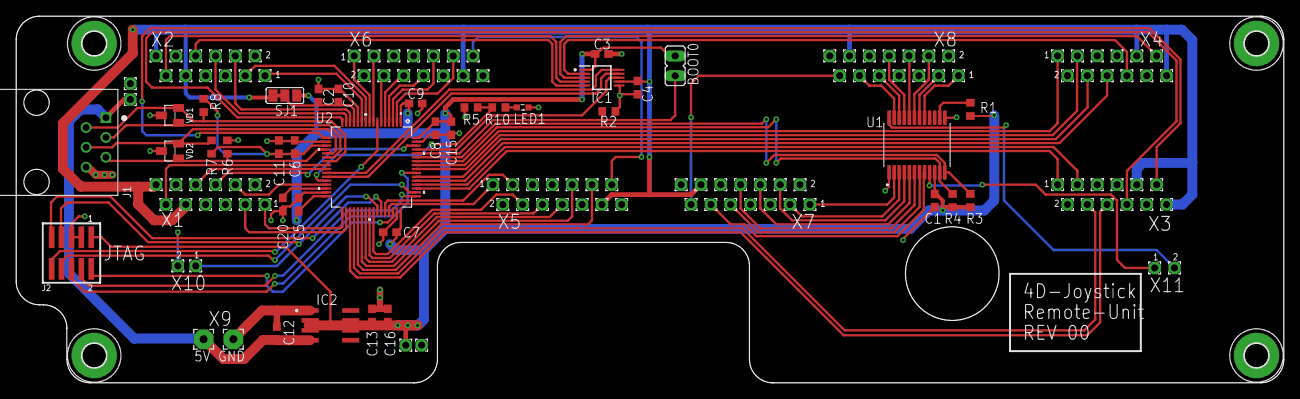
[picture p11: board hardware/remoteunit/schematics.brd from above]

Board: 2 copper layers, 162.5 x 47.0 mm, 154 parts (0 on the bottom side), 82 nets.

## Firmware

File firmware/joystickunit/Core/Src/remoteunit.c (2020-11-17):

/*******************************************************************************
 * @file         : remoteunit.c
 * @project      : 4D-Joystick, Joystick-Unit
 * @author       : Fabian Baer
 * @brief        : Handels all interactions with remote-unit
 ******************************************************************************/

/* Includes ------------------------------------------------------------------*/
#include <stdbool.h>
#include <cmsis_os.h>
#include <stm32l4xx_hal.h>
#include <board.h>
#include <system.h>
#include <remoteunit.h>
#include <configHandler.h>
#include <buttons.h>
#include <adc.h>


/* Defines -------------------------------------------------------------------*/
#define CRC_START_VALUE         0xA5


/* Macros --------------------------------------------------------------------*/
#define ADD_GPIO_BIT(gpioval, bitnum)   (((gpioval == GPIO_PIN_SET) ? 1 : 0) << bitnum)
#define EXTRACT_GPIO_VAL(data, bitnum)  ((data & (1<<bitnum)) ? GPIO_PIN_SET : GPIO_PIN_RESET)


/* Typedefs ------------------------------------------------------------------*/
typedef struct {
  //Digital
  bool teacherPort_sw3Pos;
  uint8_t teacherPort_ch1;
  uint8_t teacherPort_ch2;
  uint8_t axis_config[4];
  SysConf_Switch_t bb_config[4];
  uint8_t bb_ch1[4];
  uint8_t bb_ch2[4];

  //Analog
  Config_Analog_In_t aOut[4];
  int32_t k_num[4];
  int32_t k_den[4];
  int32_t d_low[4];
  int32_t d_high[4];
  int32_t threas_low[4];
  int32_t threas_high[4];
  int32_t middpoint_in[4];
  int32_t middpoint[4];
  bool inInverted[4];
  bool outInverted[4];
} RemUnit_Config_t;

typedef struct {
  uint32_t analog[4];
  GPIO_PinState digital[24];
} RemUnit_IOStates_t;

typedef enum {
  bbState_off = 0,
  bbState_on_1 = 1,
  bbState_on_2 = 2
} BuddyButton_State_t;


/* Prototypes ----------------------------------------------------------------*/
static void remUnit_task( void const *argument );
static void remUnit_loadConfig( RemUnit_Config_t* pConfig );
static inline void remUnit_getAxis( RemUnit_Config_t *pConfig, RemUnit_IOStates_t *pStates );
static inline void remUnit_getBuddyButtons( RemUnit_Config_t *pConfig,
    RemUnit_IOStates_t *pIOStates, BuddyButton_State_t *pBuddyStates );
static void remUnit_resetBuddyButtons( BuddyButton_State_t* pStates );
static inline void remUnit_packData( RemUnit_IOStates_t* data, uint8_t* package );
static inline void remUnit_unpackData( RemUnit_IOStates_t* pData, uint8_t* pPackage );
static uint8_t remUnit_calcCRC( uint8_t* pData, uint32_t len );
static inline bool remUnit_checkCRC( uint8_t* data, uint32_t len );


/* Variables -----------------------------------------------------------------*/
static SPI_HandleTypeDef hspi1;
extern uint32_t system_watchdog_remoteunitTask;
static osThreadId htask_remoteunit;
static osMessageQId buddyButtonsMsgBox = NULL;
static bool flag_reloadConfig = false;
static bool flag_terminateTask = false;
static bool flag_sendADC = false;
static bool flag_teacherMode = false;
static RemoteUnit_adcStates_t adcStates = {0};
static GPIO_TypeDef* const buddyButtons_ledPorts[4][2] = {
    {LED1_G_Port, LED1_R_Port},
    {LED2_G_Port, LED2_R_Port},
    {LED3_G_Port, LED3_R_Port},
    {LED4_G_Port, LED4_R_Port}};
static uint16_t const buddyButtons_ledPins[4][2] = {
    {LED1_G_Pin, LED1_R_Pin},
    {LED2_G_Pin, LED2_R_Pin},
    {LED3_G_Pin, LED3_R_Pin},
    {LED4_G_Pin, LED4_R_Pin}};
static uint8_t const crc8_table[] =   { 0x00, 0x31, 0x62, 0x53, 0xc4, 0xf5,
    0xa6, 0x97, 0xb9, 0x88, 0xdb, 0xea, 0x7d, 0x4c, 0x1f, 0x2e, 0x43, 0x72,
    0x21, 0x10, 0x87, 0xb6, 0xe5, 0xd4, 0xfa, 0xcb, 0x98, 0xa9, 0x3e, 0x0f,
    0x5c, 0x6d, 0x86, 0xb7, 0xe4, 0xd5, 0x42, 0x73, 0x20, 0x11, 0x3f, 0x0e,
    0x5d, 0x6c, 0xfb, 0xca, 0x99, 0xa8, 0xc5, 0xf4, 0xa7, 0x96, 0x01, 0x30,
    0x63, 0x52, 0x7c, 0x4d, 0x1e, 0x2f, 0xb8, 0x89, 0xda, 0xeb, 0x3d, 0x0c,
    0x5f, 0x6e, 0xf9, 0xc8, 0x9b, 0xaa, 0x84, 0xb5, 0xe6, 0xd7, 0x40, 0x71,
    0x22, 0x13, 0x7e, 0x4f, 0x1c, 0x2d, 0xba, 0x8b, 0xd8, 0xe9, 0xc7, 0xf6,
    0xa5, 0x94, 0x03, 0x32, 0x61, 0x50, 0xbb, 0x8a, 0xd9, 0xe8, 0x7f, 0x4e,
    0x1d, 0x2c, 0x02, 0x33, 0x60, 0x51, 0xc6, 0xf7, 0xa4, 0x95, 0xf8, 0xc9,
    0x9a, 0xab, 0x3c, 0x0d, 0x5e, 0x6f, 0x41, 0x70, 0x23, 0x12, 0x85, 0xb4,
    0xe7, 0xd6, 0x7a, 0x4b, 0x18, 0x29, 0xbe, 0x8f, 0xdc, 0xed, 0xc3, 0xf2,
    0xa1, 0x90, 0x07, 0x36, 0x65, 0x54, 0x39, 0x08, 0x5b, 0x6a, 0xfd, 0xcc,
    0x9f, 0xae, 0x80, 0xb1, 0xe2, 0xd3, 0x44, 0x75, 0x26, 0x17, 0xfc, 0xcd,
    0x9e, 0xaf, 0x38, 0x09, 0x5a, 0x6b, 0x45, 0x74, 0x27, 0x16, 0x81, 0xb0,
    0xe3, 0xd2, 0xbf, 0x8e, 0xdd, 0xec, 0x7b, 0x4a, 0x19, 0x28, 0x06, 0x37,
    0x64, 0x55, 0xc2, 0xf3, 0xa0, 0x91, 0x47, 0x76, 0x25, 0x14, 0x83, 0xb2,
    0xe1, 0xd0, 0xfe, 0xcf, 0x9c, 0xad, 0x3a, 0x0b, 0x58, 0x69, 0x04, 0x35,
    0x66, 0x57, 0xc0, 0xf1, 0xa2, 0x93, 0xbd, 0x8c, 0xdf, 0xee, 0x79, 0x48,
    0x1b, 0x2a, 0xc1, 0xf0, 0xa3, 0x92, 0x05, 0x34, 0x67, 0x56, 0x78, 0x49,
    0x1a, 0x2b, 0xbc, 0x8d, 0xde, 0xef, 0x82, 0xb3, 0xe0, 0xd1, 0x46, 0x77,
    0x24, 0x15, 0x3b, 0x0a, 0x59, 0x68, 0xff, 0xce, 0x9d, 0xac };


/* Code ----------------------------------------------------------------------*/

/*******************************************************************************
 * Initializes all hardware, which is related to the remote-unit:
 *  - GPIOs for SPI
 *  - GPIOs for LEDs
 *  - ADC
 *  - SPI
 *
 * @return nothing
 *******************************************************************************/
void remoteunit_init( void ) {
  GPIO_InitTypeDef GPIO_InitStruct = { 0 };

  //Enable Clocks
  __HAL_RCC_SPI1_CLK_ENABLE();
  __HAL_RCC_GPIOA_CLK_ENABLE();
  __HAL_RCC_GPIOB_CLK_ENABLE();
  __HAL_RCC_GPIOC_CLK_ENABLE();

  //Init SPI-Pins
  HAL_GPIO_WritePin(RJ12_CS_Port, RJ12_CS_Pin, GPIO_PIN_RESET);

  GPIO_InitStruct.Pin = RJ12_CS_Pin;
  GPIO_InitStruct.Mode = GPIO_MODE_OUTPUT_PP;
  GPIO_InitStruct.Pull = GPIO_NOPULL;
  GPIO_InitStruct.Speed = GPIO_SPEED_FREQ_LOW;
  HAL_GPIO_Init(GPIOA, &GPIO_InitStruct);

  GPIO_InitStruct.Pin = RJ12_SCK_Pin | RJ12_MISO_Pin | RJ12_MOSI_Pin;
  GPIO_InitStruct.Mode = GPIO_MODE_AF_PP;
  GPIO_InitStruct.Pull = GPIO_NOPULL;
  GPIO_InitStruct.Speed = GPIO_SPEED_FREQ_VERY_HIGH;
  GPIO_InitStruct.Alternate = GPIO_AF5_SPI1;
  HAL_GPIO_Init(GPIOA, &GPIO_InitStruct);

  //Init LED-Pins
  HAL_GPIO_WritePin(GPIOB, LED2_G_Pin | LED2_R_Pin | LED3_G_Pin | LED3_R_Pin, GPIO_PIN_RESET);
  HAL_GPIO_WritePin(GPIOC, LED4_G_Pin | LED1_G_Pin | LED1_R_Pin, GPIO_PIN_RESET);
  HAL_GPIO_WritePin(GPIOA, LED4_R_Pin, GPIO_PIN_RESET);

  GPIO_InitStruct.Pin = LED4_R_Pin;
  GPIO_InitStruct.Mode = GPIO_MODE_OUTPUT_PP;
  GPIO_InitStruct.Pull = GPIO_NOPULL;
  GPIO_InitStruct.Speed = GPIO_SPEED_FREQ_LOW;
  HAL_GPIO_Init(GPIOA, &GPIO_InitStruct);

  GPIO_InitStruct.Pin = LED2_G_Pin | LED2_R_Pin | LED3_G_Pin | LED3_R_Pin;
  GPIO_InitStruct.Mode = GPIO_MODE_OUTPUT_PP;
  GPIO_InitStruct.Pull = GPIO_NOPULL;
  GPIO_InitStruct.Speed = GPIO_SPEED_FREQ_LOW;
  HAL_GPIO_Init(GPIOB, &GPIO_InitStruct);

  GPIO_InitStruct.Pin = LED4_G_Pin | LED1_G_Pin | LED1_R_Pin;
  GPIO_InitStruct.Mode = GPIO_MODE_OUTPUT_PP;
  GPIO_InitStruct.Pull = GPIO_NOPULL;
  GPIO_InitStruct.Speed = GPIO_SPEED_FREQ_LOW;
  HAL_GPIO_Init(GPIOC, &GPIO_InitStruct);

  //Init SPI
  hspi1.Instance = SPI1;
  hspi1.Init.Mode = SPI_MODE_MASTER;
  hspi1.Init.Direction = SPI_DIRECTION_2LINES;
  hspi1.Init.DataSize = SPI_DATASIZE_8BIT;
  hspi1.Init.CLKPolarity = SPI_POLARITY_LOW;
  hspi1.Init.CLKPhase = SPI_PHASE_1EDGE;
  hspi1.Init.NSS = SPI_NSS_SOFT;
  hspi1.Init.BaudRatePrescaler = SPI_BAUDRATEPRESCALER_256;
  hspi1.Init.FirstBit = SPI_FIRSTBIT_LSB;
  hspi1.Init.TIMode = SPI_TIMODE_DISABLE;
  hspi1.Init.CRCCalculation = SPI_CRCCALCULATION_DISABLE;
  hspi1.Init.CRCPolynomial = 15;
  hspi1.Init.CRCLength = SPI_CRC_LENGTH_DATASIZE;
  hspi1.Init.NSSPMode = SPI_NSS_PULSE_DISABLE;

  if (HAL_SPI_Init(&hspi1) != HAL_OK) {
    system_errorHandler();
  }
}


/*******************************************************************************
 * Set the message queue, which provides status of the buddybuttons.
 *
 * @param msgQueue The buddybuttons message queue
 * @return nothing
 *******************************************************************************/
void remoteunit_setBuddyButtonsMQ( osMessageQId msgQueue ) {
  buddyButtonsMsgBox = msgQueue;
}


/*******************************************************************************
 * Initializes the task.
 *
 * @param priority The task priority
 * @return nothing
 *******************************************************************************/
void remoteunit_setupTask( osPriority priority ) {
  osThreadDef(remoteunitTask, remUnit_task, priority, 0, 512);
  htask_remoteunit = osThreadCreate(osThread(remoteunitTask), NULL);
}


/*******************************************************************************
 * Terminates the task (after the end of the next execution).
 *
 * @return nothing
 *******************************************************************************/
void remoteunit_terminateTask( void ) {
  flag_terminateTask = true;
}
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

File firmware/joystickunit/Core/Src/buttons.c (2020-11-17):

/*******************************************************************************
* @file         : buttons.c
* @project      : 4D-Joystick, Joystick-Unit
* @author       : Fabian Baer
* @brief        : Handles debouncing of the buddybuttons and rotary encoder
*******************************************************************************/

/* Includes ------------------------------------------------------------------*/
#include <stdbool.h>
#include <cmsis_os.h>
#include <stm32l4xx_hal.h>
#include <board.h>
#include <system.h>
#include <buttons.h>


/* Typedefs ------------------------------------------------------------------*/
typedef enum {
  btnFSM_risingEdge,
  btnFSM_high_hold,
  btnFSM_high,
  btnFSM_fallingEdge,
  btnFSM_low_hold,
  btnFSM_low
} ButtonFSM_t;

typedef enum {
  btnState_fallingEdge,
  btnState_low,
  btnState_risingEdge,
  btnState_high
} ButtonState_t;

typedef struct {
  ButtonFSM_t statemachine;
  ButtonState_t state;
  uint32_t timeout;
  uint32_t holdTime;
  GPIO_TypeDef* port;
  uint16_t pin;
} Button_t;

//Check if Message-Unions have the size of an uint32_t
typedef uint8_t assertBuddyMsgSize[(sizeof(BuddyButtonMessage_t)==4)*2-1 ];
typedef uint8_t assertRotaryMsgSize[(sizeof(RotaryEncoderMessage_t)==4)*2-1 ];


/* Prototypes ----------------------------------------------------------------*/
static void buttons_task( void const *argument );
static void buttons_initStruct( Button_t* pBtn, uint32_t holdTime, GPIO_TypeDef* port, uint16_t pin );
static void buttons_statemachine( Button_t* pBtn );
static void buttons_handleBuddyButton( Button_t* pBtn, Config_BuddyButton_t buddyId );
static inline void buttons_handleRotaryEncoder( Button_t* pRot1, Button_t* pRot2, Button_t* pRotP );


/* Variables -----------------------------------------------------------------*/
osThreadId htask_buttons;
osMessageQDef(buddyButtonsMsgBox, 32, BuddyButtonMessage_t);
osMessageQId buddyButtonsMsgBox;
osMessageQDef(rotaryEncoderMsgBox, 32, RotaryEncoderMessage_t);
osMessageQId rotaryEncoderMsgBox;
extern uint32_t system_watchdog_buttonTask;

/* Code ----------------------------------------------------------------------*/

/*******************************************************************************
 * Initializes all GPIOs and message queues for the buttons.
 *
 * @return nothing
 *******************************************************************************/
void buttons_init( void ) {
  GPIO_InitTypeDef GPIO_InitStruct = { 0 };

  GPIO_InitStruct.Pin = BB_4_Pin | BB_3_Pin | BB_2_Pin | BB_1_Pin | BTN3_Pin
      | BTN2_Pin | BTN1_Pin;
  GPIO_InitStruct.Mode = GPIO_MODE_INPUT;
  GPIO_InitStruct.Pull = GPIO_PULLUP;
  HAL_GPIO_Init(GPIOC, &GPIO_InitStruct);

  buddyButtonsMsgBox = osMessageCreate(osMessageQ(buddyButtonsMsgBox), NULL);
  rotaryEncoderMsgBox = osMessageCreate(osMessageQ(rotaryEncoderMsgBox), NULL);
}


/*******************************************************************************
 * Returns the handle of the buddybutton message queue.
 *
 * @return buddybutton message queue
 *******************************************************************************/
osMessageQId buttons_getBuddyButtonsMQ( void ) {
  return buddyButtonsMsgBox;
}


/*******************************************************************************
 * Returns the handle of the rotary encoder message queue.
 *
 * @return rotary encoder message queue
 *******************************************************************************/
osMessageQId buttons_getRotaryEncoderMQ( void ) {
  return rotaryEncoderMsgBox;
}


/*******************************************************************************
 * Initializes the task.
 *
 * @param priority The task priority
 * @return nothing
 *******************************************************************************/
void buttons_setupTask( osPriority priority ) {
  osThreadDef(buttonsTask, buttons_task, priority, 0, 512);
  htask_buttons = osThreadCreate(osThread(buttonsTask), NULL);
}


/*******************************************************************************
 * The buttons-task.
 * This task handles the buttons statemachine, which is responsible for
 * debouncing and edge detection.
 *
 * @return nothing
 *******************************************************************************/
static void buttons_task( void const *argument ) {
  (void)argument;
  Button_t bb1, bb2, bb3, bb4, rotP, rot1, rot2;

  //Initialize structs
  buttons_initStruct(&bb1, 50, BB_1_Port, BB_1_Pin);
  buttons_initStruct(&bb2, 50, BB_2_Port, BB_2_Pin);
  buttons_initStruct(&bb3, 50, BB_3_Port, BB_3_Pin);
  buttons_initStruct(&bb4, 50, BB_4_Port, BB_4_Pin);
  buttons_initStruct(&rot1, 1, BTN2_Port, BTN2_Pin);
  buttons_initStruct(&rot2, 1, BTN3_Port, BTN3_Pin);
  buttons_initStruct(&rotP, 1, BTN1_Port, BTN1_Pin);

  while(1) {
    buttons_handleBuddyButton(&bb1, buddyButton1);
    buttons_handleBuddyButton(&bb2, buddyButton2);
    buttons_handleBuddyButton(&bb3, buddyButton3);
    buttons_handleBuddyButton(&bb4, buddyButton4);

    buttons_handleRotaryEncoder(&rot1, &rot2, &rotP);

    system_watchdog_buttonTask++;
    osDelay(2);
  }
}


/*******************************************************************************
 * Initializes the button-struct with default values.
 *
 * @param pBtn A pointer to the used button-struct
 * @param holdTime Time where transitions are blocked, after a transition
 * @param port The port of the button GPIO
 * @param pin The pin of the button GPIO
 * @return nothing
 *******************************************************************************/
static void buttons_initStruct( Button_t* pBtn, uint32_t holdTime, GPIO_TypeDef* port, uint16_t pin ) {
  pBtn->statemachine = btnFSM_high;
  pBtn->timeout = 0;
  pBtn->holdTime = holdTime;
  pBtn->port = port;
  pBtn->pin = pin;
}
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

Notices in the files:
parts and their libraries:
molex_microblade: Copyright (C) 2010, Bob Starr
